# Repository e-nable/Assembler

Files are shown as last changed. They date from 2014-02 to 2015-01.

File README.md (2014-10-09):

e-NABLE Assembler (AKA Hand-o-Matic)
=======

repository for OpenSCAD scripts (and referenced STL files) for e-NABLE Assembler project

Overall control flow is:



This repository contains the Assembly.scad and it's dependencies, such as the STL files for all of the e-NABLE designs. These include:

- Assembly assembles parts from individual designs (below)
- Cyborg_Beast
- Parametric_Gauntlet
- Parametric Tensioner
- Parametric Knuckle Block
- David Finger
- Talon (placeholder)

Parameters
========
part
- 0 Assembled Model
- 1 Gauntlet
- 2 Palm
- 3 Finger Proximal (Near knuckle)
- 4 Finger Distal (Fingertip)
- 5 Thumb Proximal (Near knuckle)
- 6 Thumb Distal (Thumbtip)

Finger Style
- 1 Cyborg Beast
- 2 David
- 3 Creo Cyborg Beast

Palm Style
- 1 Cyborg Beast
- 2 Cyborg Beast Parametric
- 3 Creo Cyborg Beast

Example
======
openscad -o preview.png -D Left1=66.47 -D Left2=64.04 -D  Left3=46.95 -D  Left4=35.14 -D  Left5=35.97 -D  Left6=27.27 -D  Left7=31.80 -D  Left8=40.97 -D  Left9=31.06 -D  Left10=147.5 -D Right1=62.67 -D Right2=65.62 -D  Right3=59.14 -D  Right4=48.78 -D  Right5=51.85 -D  Right6=16.4 -D  Right7=0 -D  Right8=72.52 -D  Right9=72.23 -D  Right10=230.6  -D part=0 -D fingerSelect=1 -D palmSelect=2 -D WristBolt=5.5 -D KnuckleBolt=3.3 -D JointBolt=3.3 -D ThumbBolt=3.3   e-NABLE/Assembly/Assembly.scad

Prerequisites
=========
OpenScad as ran on command line. Download from openscad.org

On a 'headless' server, you may need to set up a virtual container for the program to render into. The code below is to be ran on the command line before you run the comand line openscad. It may not work on your server. A google search found this example, your system may need something else.

Xvfb :5 -screen 0 800x600x24 &
export DISPLAY=:5

See Also
=========
The e-NABLE Assembler is utilized by the e-NABLE Service Station (AKA Hand-o-Matic) at https://github.com/e-nable/Service-Station .

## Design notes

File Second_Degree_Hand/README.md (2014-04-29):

Second Degree Hand by David
===========================

http://www.thingiverse.com/thing:300499

This is a mechanical hand made for users with a functional thumb. It includes an opening that allows the user to utilize their thumb along with mechanical fingers.

This hand includes a couple of unusual features:

First, this hand allows for two degrees of freedom in the motion. Most similar hands only allow the user to raise or lower the fingers. This one also allows the user to move the fingers side-to-side. A demonstration of the two degrees of freedom can be seen at:

http://youtu.be/62XzqfjZZns

Second, this hand includes springs on the tuners. This resolves some issues so that the hand has dramatically improved grip. A demonstration of this feature can be seen at:

http://youtu.be/e6_-tVWOsLo

This design is also fully parametric OpenSCAD files. Although there are STL files attached, they are just for example purposes. The intention is that each individual will create their own unique STLs from the SCAD files.

There is currently no option for a mechanical thumb in this design. There are a couple of other hand designs that include a mechanical thumb. If someone really wants a thumb added to this design (maybe because of the two degrees of freedom) I can maybe add it.

I am not marking this one a work in progress. The one I was making for my sister is pretty much complete and working well. I am working on an updated version, but that will likely be a new version 3.

As always... This is provided in the hope that it will be beneficial. It is provided, however, without any warranty of any sort. Use at your own risk, and seek appropriate medical attention. If you do use it, and you experience any problems, immediately discontinue use.

For more information on where to connect with people who can help someone in need with sizing, printing and/or assembly of a mechanical hand please join the e-NABLE Google+ Community entitled, e-NABLE: 
https://plus.google.com/communities/102497715636887179986 
For more information and stories: 
http://enablingthefuture.org 
https://www.facebook.com/enableorganization

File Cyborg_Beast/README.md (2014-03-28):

e-nable : Cyborg Beast
======================

Repository for Cyborg Beast files.

- Blender Files are the source files
- STL files are rendered for printing
- OpenSCAD files assemble the STL files for parametric rendering

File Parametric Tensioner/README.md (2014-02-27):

Parametric Cable Tensioner
==========================

See http://www.thingiverse.com/thing:238852 for originals.

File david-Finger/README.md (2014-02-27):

Parametric Finger
=================

See http://www.thingiverse.com/thing:257544 for originals.

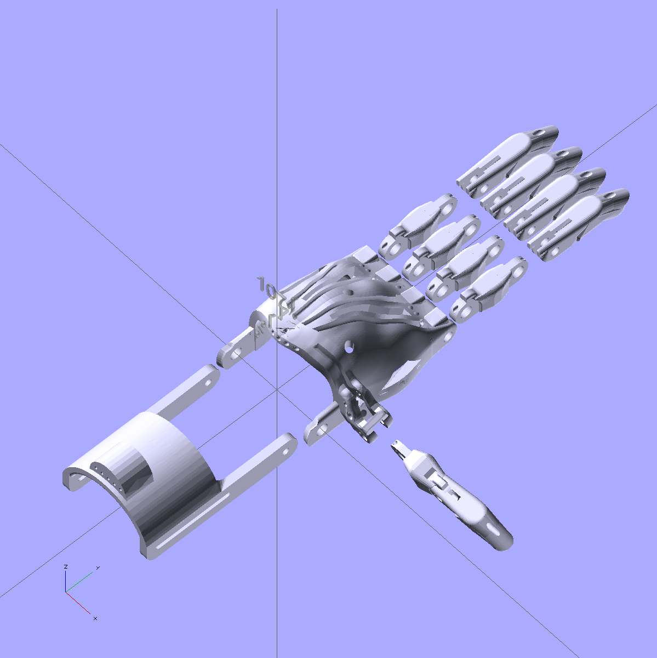
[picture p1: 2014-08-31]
explode2.png

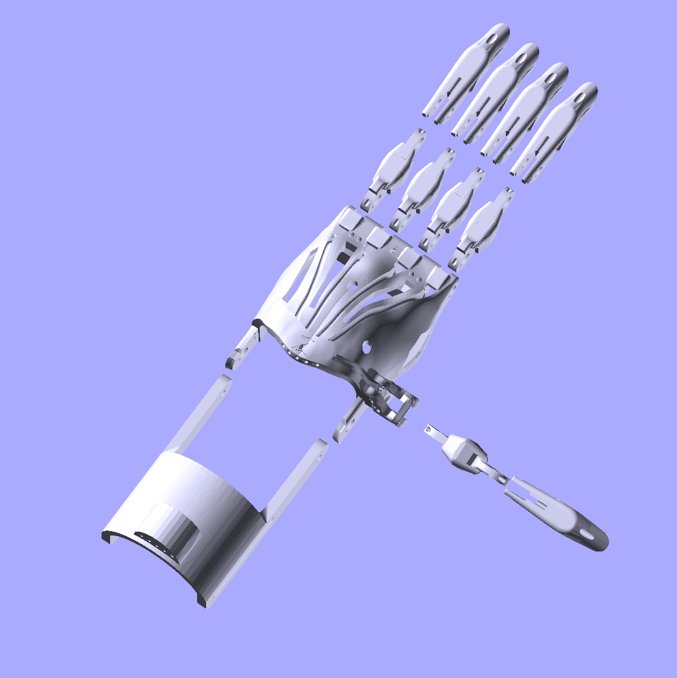
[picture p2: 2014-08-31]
exploded-image.png

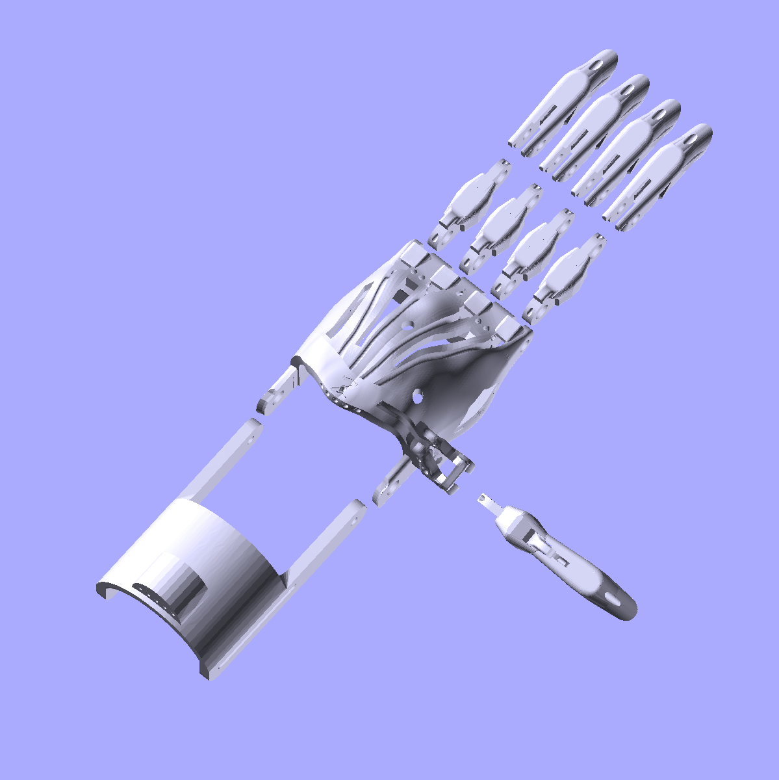
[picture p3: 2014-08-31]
explode3.png

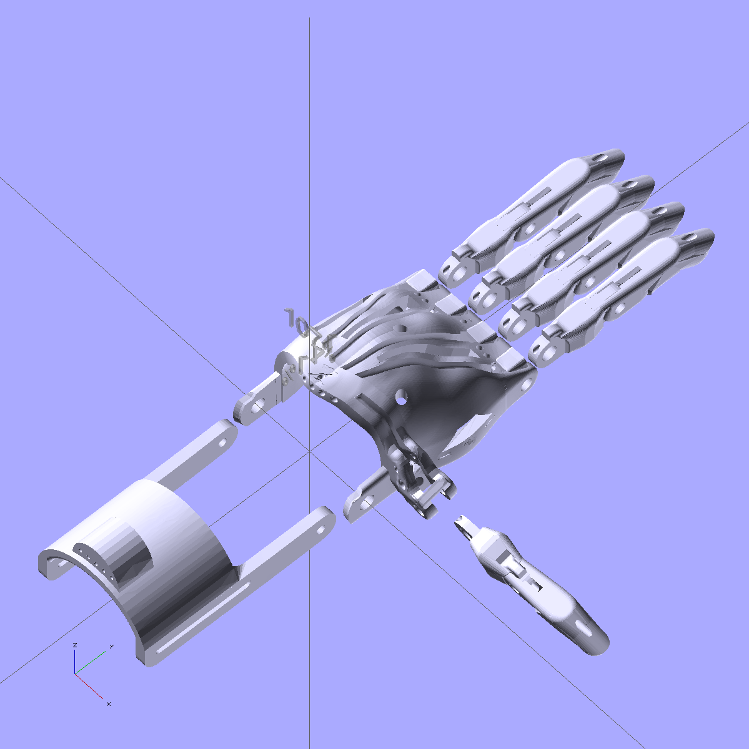
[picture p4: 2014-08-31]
exploded.png

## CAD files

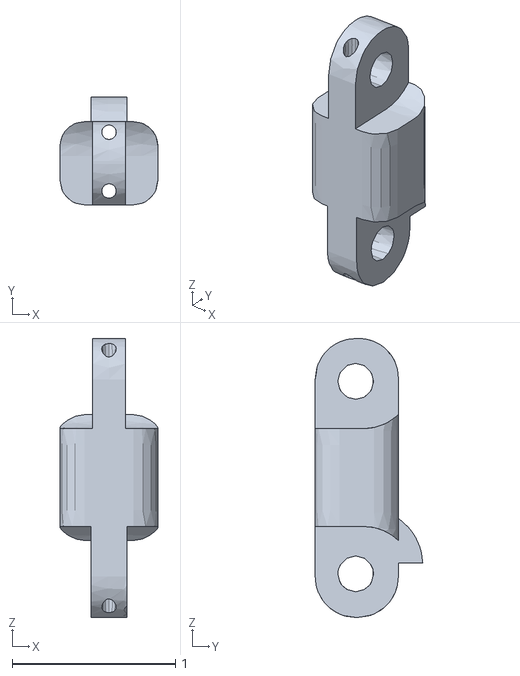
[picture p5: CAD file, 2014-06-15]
Cyborg_Beast/Creo_Cyborg_Beast/finger_mid_joint.stl
0.6 x 0.66 x 1.71

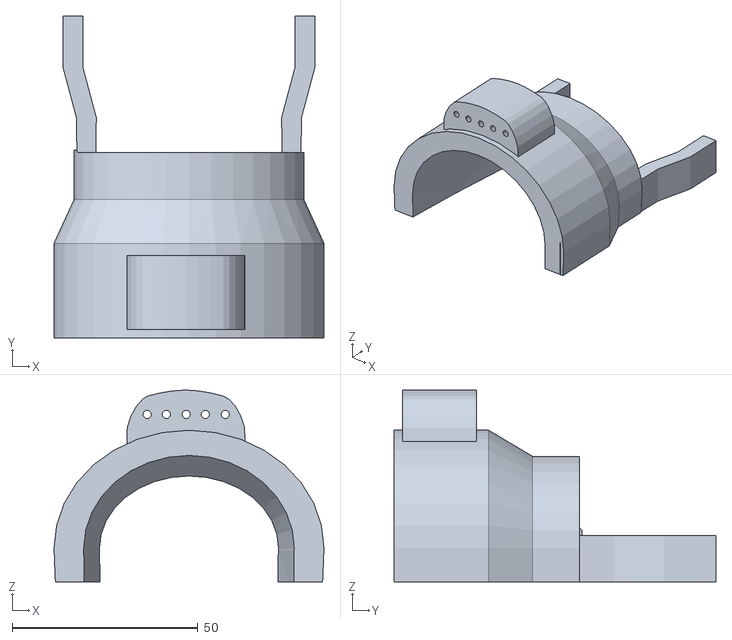
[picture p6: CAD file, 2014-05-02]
Cyborg_Beast/STL Files/Cyborg Hand 1.2/Cyborg gauntlet 1.2 (Ivan).stl
72.7 x 86.6 x 51.7

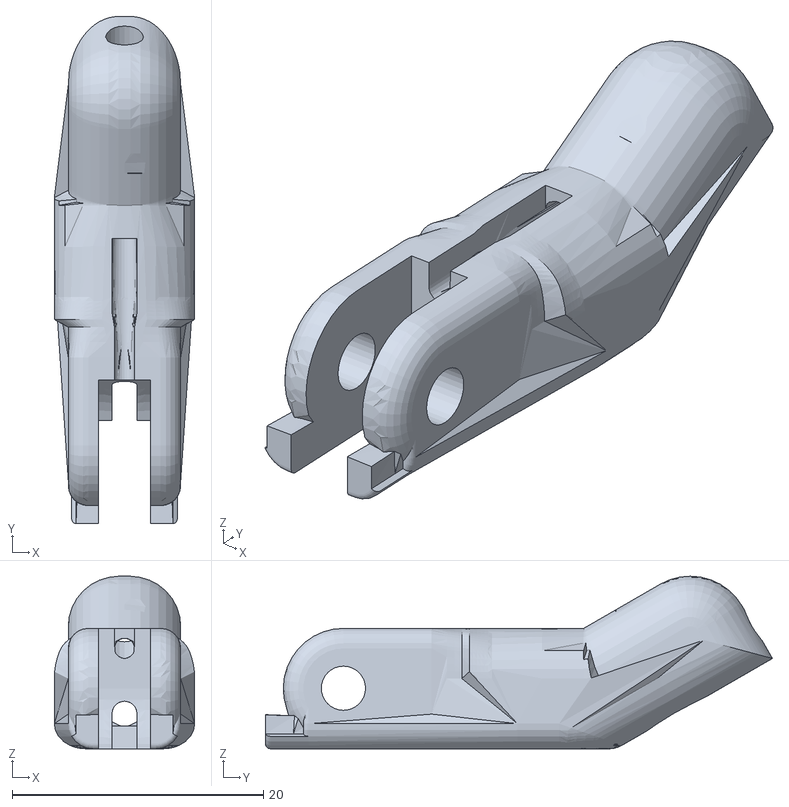
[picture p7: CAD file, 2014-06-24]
Cyborg_Beast/STL Files/Cyborg Hand 1.4/CB Finger 1.41 (no bumps).stl
11.2 x 40.3 x 13.7

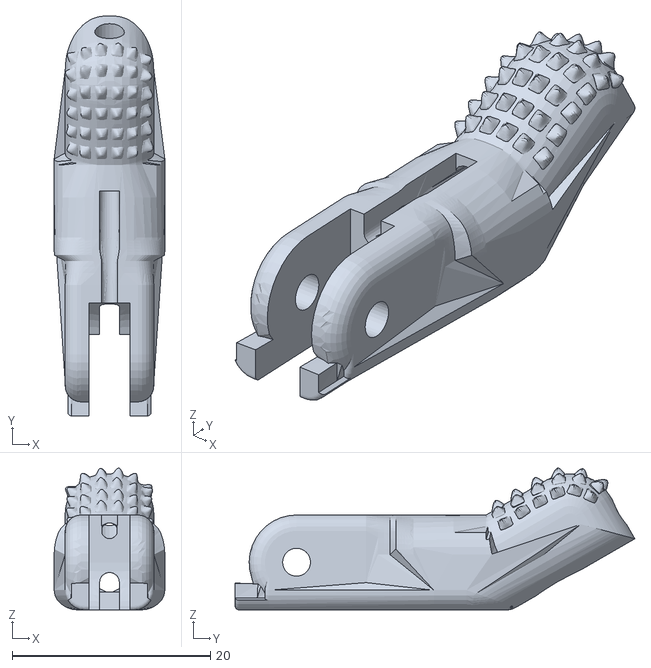
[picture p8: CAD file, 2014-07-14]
Cyborg_Beast/STL Files/Cyborg Hand 1.45 No Thumb/CB_Finger (bumps) Non-Manifold 1.45.stl
11.2 x 40.3 x 14.3

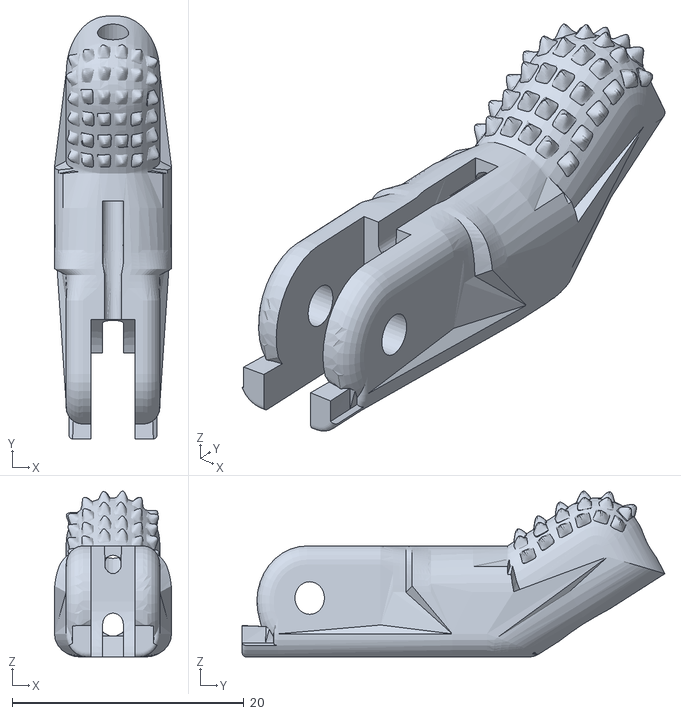
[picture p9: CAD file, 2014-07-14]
Cyborg_Beast/STL Files/Cyborg Hand 1.45/CB_Thumb_Finger (bumps) Non-Manifold 1.45.stl
10.1 x 36.5 x 14.3

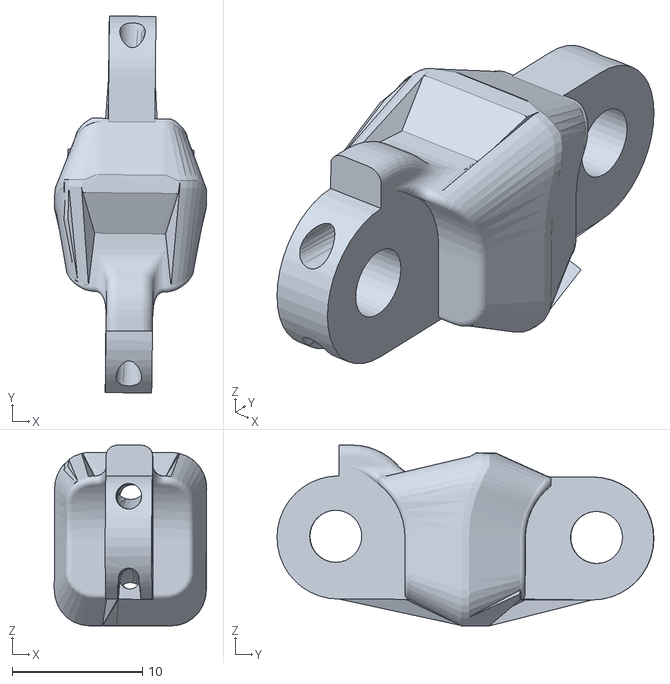
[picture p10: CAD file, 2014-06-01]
Cyborg_Beast/STL Files/Cyborg_Beast_Peter_Binkleys_Fix/ProxThumb.stl
11.7 x 28.9 x 13.9

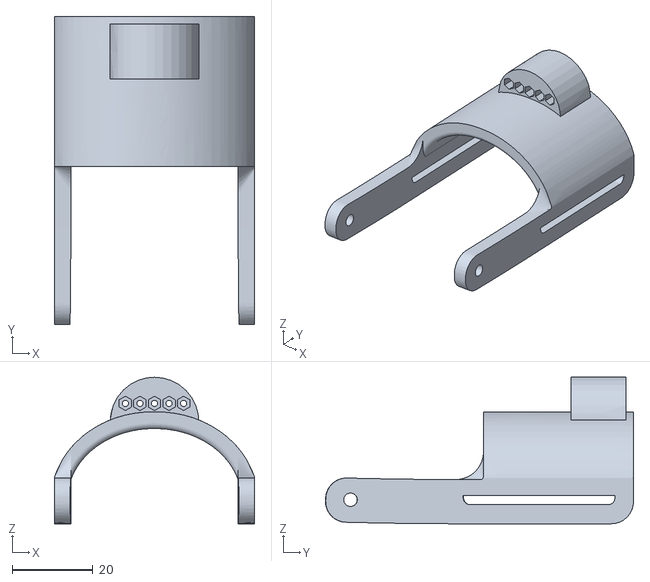
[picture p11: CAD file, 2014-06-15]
Cyborg_Beast/STL Files/Karunas_Short_Gauntlet.stl
49.6 x 76.3 x 36.3

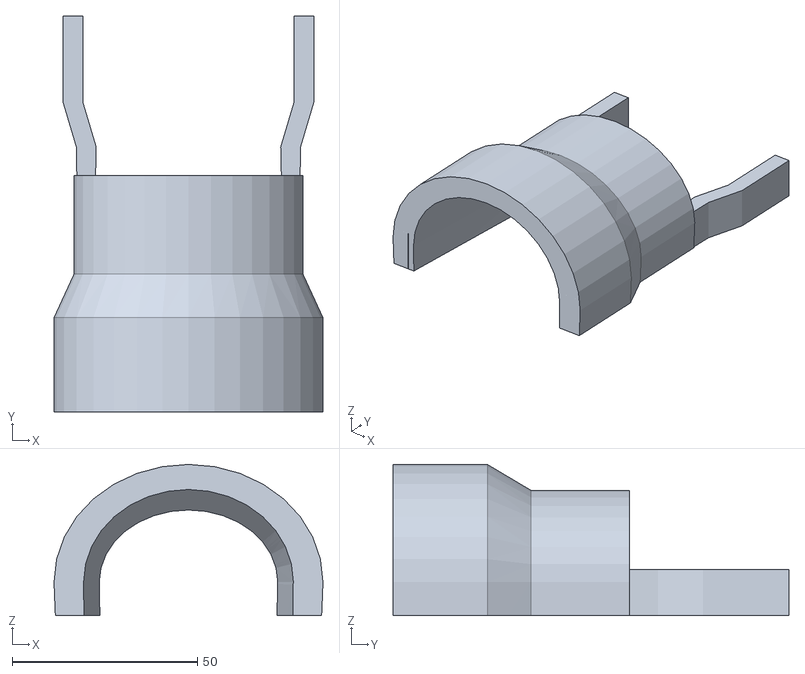
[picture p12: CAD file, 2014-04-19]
Cyborg_Beast/STL Files/STL Files_ Marc Petrykowski_4-16-2014/Cyborg Gauntlet 1.1.stl
72.7 x 106.9 x 40.8

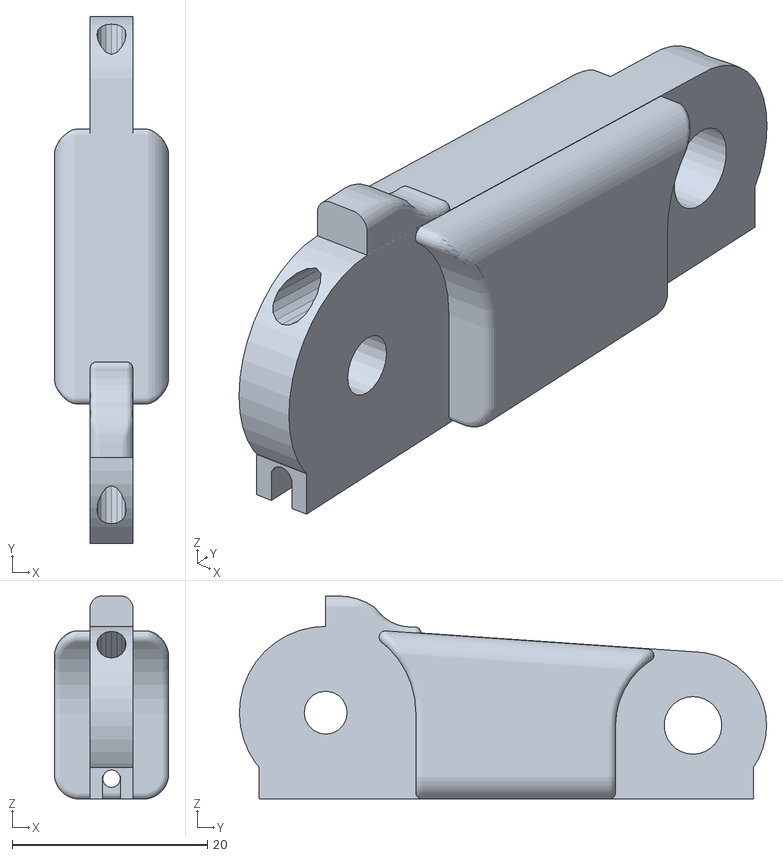
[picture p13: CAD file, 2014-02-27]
david-Finger/David-FingerProximal-Index.stl
11.7 x 54.0 x 20.8

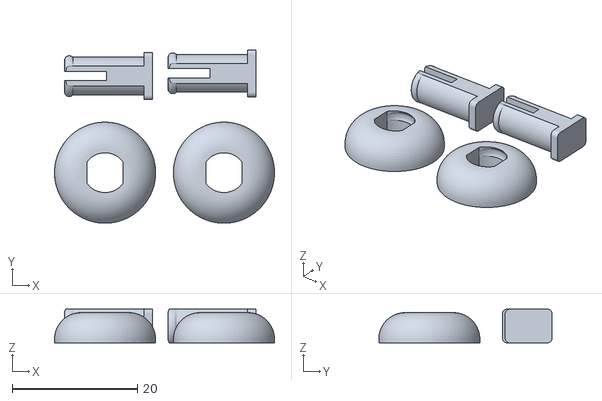
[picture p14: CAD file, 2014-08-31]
EH2.0/non-aligned/EH2.0_Gauntlet_Ware_2.5 (2 of 3).stl
35.2 x 27.7 x 5.40

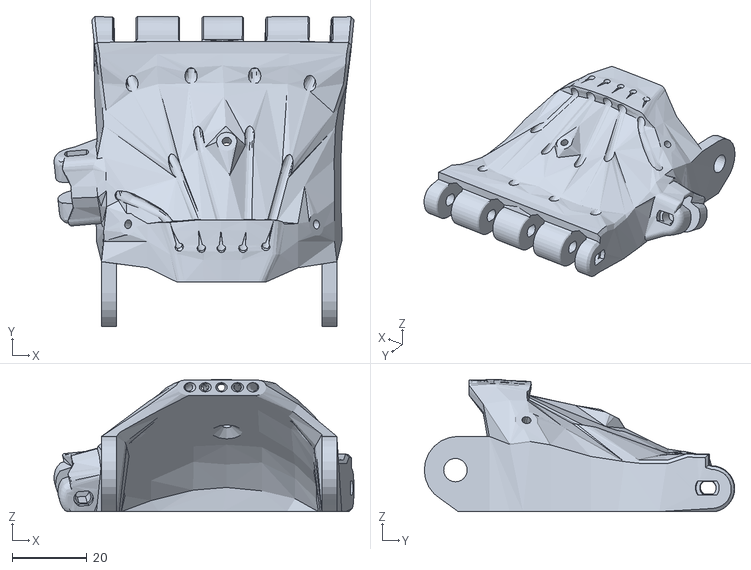
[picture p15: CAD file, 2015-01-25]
EH2.0/RaptorPalmRightNoSup_2.22.stl
80.3 x 83.1 x 35.4

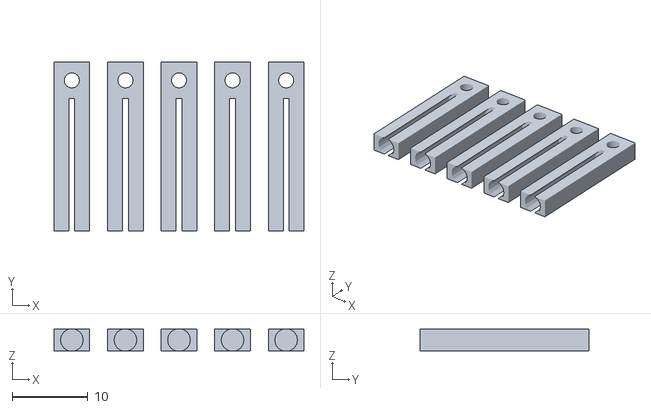
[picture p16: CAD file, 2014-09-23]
EH2.0/TensionerPins/TensionerPins-3mm.stl
32.9 x 22.2 x 2.85

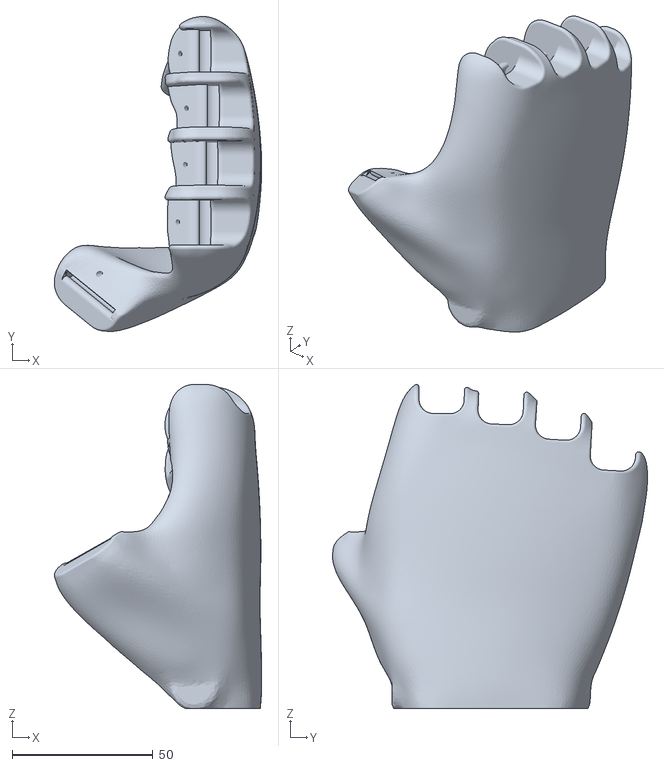
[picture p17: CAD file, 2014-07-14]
Flexy-Hand_2-2/Hand_Body_-_RH.stl
73.6 x 111.7 x 114.9

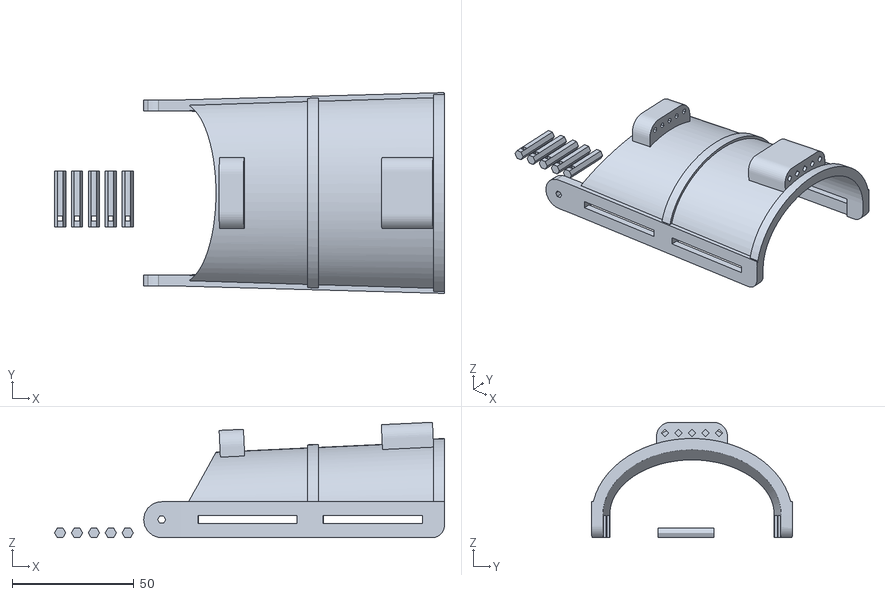
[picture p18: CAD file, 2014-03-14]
Parametric_Gauntlet/David-Gauntlet-5M2.stl
160.0 x 82.4 x 47.4

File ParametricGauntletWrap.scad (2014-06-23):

/* [Measurements] */
// See Measurement Guide at:
// https://docs.google.com/a/popk.in/document/d/1LX3tBpio-6IsMMo3aaUdR-mLwWdv1jS4ooeEHb79JYo for details.
// The default values are the ones from the photo in that document.

// e-NABLE measurement 5, Wrist Joint distance from lateral to medial side
wrist = 35.97;
// Length of gauntlet, e.g. half distance from elbow to wrist.
len = 100;
// Distance between lateral and medial side of the middle forearm (end of gauntlet closest to elbow)
width = 46.35;
// height of side rail
rail = 10; 
// thickness of side rails
thick=5; 
// thickness of rest of gauntlet
thin=2; 
// thickness of padding
padding = 5;
// spacing of bars
spacing = 10;
// thickness of bars
bar=5;
// diameter of bolt for wrist pivot
bolt = 5;
// Length of slots
slotLen = 25;
// Height of slots
slotH = 2;

/* [hidden] */

pi=3.1415926;

wristX = (wrist+2*padding)*pi/2-rail/2;
wideX = (width+2*padding)*pi/2-rail/2;

diff = wideX-wristX;
angle = atan(diff/len);
echo(diff,angle);

echo(len, wristX, wideX);

difference() {
union() {
difference() {
	union() {
		hull() {
			translate([wristX,0]) cylinder(d=rail, h=thick);
			translate([wideX,-len]) cylinder(d=rail, h=thick);
			}
		hull() {
			translate([-wristX,0]) cylinder(d=rail, h=thick);
			translate([-wideX,-len]) cylinder(d=rail, h=thick);
			}
		scale([3,1,1])hull() {
			translate([0,-(wristX)]) cylinder(d=rail, h=thin);
			translate([0,-len]) cylinder(d=rail, h=thin);
			}
		difference() {
			hull() {
				translate([wristX,-bar]) cylinder(d=rail, h=thin);
				translate([wideX,-len]) cylinder(d=rail, h=thin);
				translate([-wristX,-bar]) cylinder(d=rail, h=thin);
				translate([-wideX,-len]) cylinder(d=rail, h=thin);
				}
			translate([0,0,-1]) cylinder(r=wristX-rail/2, h=thick+2);
			translate([0,0,-.5]) for (r=[wristX-rail/2+bar:spacing:len+3*spacing]) {
				core(r,bar,thin+1);
				}
			}
		}
	}

hull() {
	translate([-wideX,-len]) cylinder(d=rail, h=thin);
	translate([wideX,-len]) cylinder(d=rail, h=thin);
	}
}
	translate([wristX,0,-2]) cylinder(d=bolt, h=thick+4);
	translate([-wristX,0,-2]) cylinder(d=bolt, h=thick+4);
	translate([wideX,-len,-1]) rotate([0,0,angle]) cube([2,25,thick+2]);
	translate([-wideX-slotH,-len,-1]) rotate([0,0,-angle]) cube([2,25,thick+2]);
	translate([wideX-diff/3,-len*.67,-1]) rotate([0,0,angle]) cube([slotH,25,thick+2]);
	translate([-wideX+diff/3-slotH,-len*.67,-1]) rotate([0,0,-angle]) cube([slotH,25,thick+2]);
	translate([wideX-diff*.67,-len/3,-1]) rotate([0,0,angle]) cube([slotH,25,thick+2]);
	translate([-wideX+diff*.67-slotH,-len/3,-1]) rotate([0,0,-angle]) cube([slotH,25,thick+2]);

}


module core(r,t,h) {
	difference() {
		cylinder(r=r+t, h=h);
		translate([0,0,-1]) cylinder(r=r, h=h+1);
		}
	}

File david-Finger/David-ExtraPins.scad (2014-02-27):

/*

Extra Pins for Parametric Fingers
By David Orgeman

licensed under the Creative Commons - Attribution - Share Alike license

This program is distributed in the hope that it will be useful,
but WITHOUT ANY WARRANTY; without even the implied warranty of
MERCHANTABILITY or FITNESS FOR A PARTICULAR PURPOSE.

*/



//PARAMETERS

//Pin_Head_Height is the size of the thickness of the head on the pin.
Pin_Head_Height=1.4;

//Knuckle_Hole_Size is the hole for the link between distal and proximal phalanges.  Set this
//to the diameter or the pin.  Pins with larger diameter work better.
Knuckle_Hole_Size=5.0;

//Set Scale_Factor to match the scaling of the other prosthetic parts.
Scale_Factor=1.3;


//RENDER

translate([20, -10, 0])
	custom_pin();
translate([0, -10, 0])
	custom_pin();
translate([-20, -10, 0])
	custom_pin();
translate([10, 10, 0])
	custom_pin();
translate([-10, 10, 0])
	custom_pin();


module custom_pin()
	{
	pin_horizontal(h=9*Scale_Factor, lh=1.7, lt=1.0, r=Knuckle_Hole_Size/2, tight=false);
	translate([0, 9*Scale_Factor/2, (Knuckle_Hole_Size-0.5)/2])
		rotate(a=[90, 0, 0])
			difference()
				{
				cylinder(h=Pin_Head_Height, r=1.5*Knuckle_Hole_Size/2, $fn=16);
				translate([-5, -10-Knuckle_Hole_Size/2+0.375, -5])
					cube([10, 10, 10]);
				translate([-5, Knuckle_Hole_Size/2-0.375, -5])
					cube([10, 10, 10]);
				}
	}

	
	
module fillet(r, h) 
	{
	translate([r/2, r/2, 0])
		difference() 
			{
			cube([r, r, h], center=true);
			translate([r/2, r/2, 0])
				cylinder(h=h+1, r=r, center=true, $fn=40);
			}
	}



module fillet_bez(r, h, a=90) 
	{
	p0=[r, 0];
	p1=[0, 0];
	p2=[r*cos(a), r*sin(a)];
	translate([0, 0, -h/2])
		linear_extrude(height=h) BezConic(p0, p1, p2, 32);
	}



//Polyhole module by nophead
//licensed under the Creative Commons - Attribution license
//provided here, as-is, without any warranty of any sort
//original work available at http://www.thingiverse.com/thing:6118
//and also at http://hydraraptor.blogspot.com/2011/02/polyholes.html

module polyhole(d, h) 
	{
	n=max(round(2*d), 3);
	rotate(v=[0, 0, 180])
		cylinder(h=h, r=(d/2)/cos(180/n), center=true, $fn=n);
	}



//OpenSCAD Conic Bezier Curve by donb
//licensed under the Creative Commons - Public Domain license - no rights reserved
//provided here, as-is, without any warranty of any sort
//original work available at http://www.thingiverse.com/thing:8931

/* 
Conic Bezier Curve
also known as Quadratic Bezier Curve
also known as Bezier Curve with 3 control points 

Please see 
http://www.thingiverse.com/thing:8443 by William A Adams
http://en.wikipedia.org/wiki/File:Bezier_2_big.gif by Phil Tregoning
http://en.wikipedia.org/wiki/B%C3%A9zier_curve by Wikipedia editors

By Don B, 2011, released into the Public Domain
*/

module BezConic(p0, p1, p2, steps=5) {

	stepsize1 = (p1-p0)/steps;
	stepsize2 = (p2-p1)/steps;

	for (i=[0 : steps-1]) {
		assign(point1 = p0+stepsize1*i) 
		assign(point2 = p1+stepsize2*i) 
		assign(point3 = p0+stepsize1*(i+1))
		assign(point4 = p1+stepsize2*(i+1))  {
			assign( bpoint1 = point1+(point2-point1)*(i/steps) )
			assign( bpoint2 = point3+(point4-point3)*((i+1)/steps) ) {
				polygon(points=[bpoint1, bpoint2, p1]);
			}
		}
	}
}



//"PLA Pin Connectors v2" by whpthomas
//licensed under the Creative Commons - Attribution - Share Alike license
//modified so the module creates a rounder pin at small sizes
//modified to make some primitives overlap so that the stl has fewer errors
//provided as-is, without any warranty of any sort
//original work available at http://www.thingiverse.com/thing:130879

// PLA Pin Connectors
// WHPThomas <me@henri.net>
// Derived to provide a drop in replacement for Tony Buser's pin connectors <tbuser@gmail.com>

//pinhole(h=12, tight=false);
//test();
//pintack(h=20);
//pinpeg(h=24);

module test() {
  tolerance = 0.2;
  radius=7/2;
  
  translate([-12, 16, 0]) pinpeg(h=21, r=radius);
  translate([12, 12, 0]) pintack(h=12, r=radius);
  
  difference() {
    union() {
      translate([0, -12, 2.5]) cube(size = [60, 20, 5], center = true);
      translate([24, -12, 7.5]) cube(size = [12, 20, 15], center = true);
    }
    translate([-24, -12, 0]) pinhole(h=5, r=radius, t=tolerance);
    translate([-12, -12, 0]) pinhole(h=5, r=radius, t=tolerance, tight=false);
    translate([0, -12, 0]) pinhole(h=16, r=radius, t=tolerance);
    translate([12, -12, 0]) pinhole(h=16, r=radius, t=tolerance, tight=false);
    translate([24, -12, 15]) rotate([0, 180, 0]) pinhole(h=12, r=radius, t=tolerance);
  }
}

module pinhole(h=16, r=4, lh=3, lt=1, t=0.3, tight=true) {
  // h = shaft height
  // r = shaft radius
  // lh = lip height
  // lt = lip thickness
  // t = tolerance
  // tight = set to false if you want a joint that spins easily
  union() {
    pin_solid(h, r+(t/2), lh, lt);
    if (tight) {
      // make the cylinder slightly longer
      cylinder(h=h+t, r=r, $fn=30);
    }
    else {
      // make the cylinder slightly longer and wider
      cylinder(h=h+t, r=r+(t/2)+t, $fn=30);
    }
    // camfer the entrance hole to make insertion easier
    translate([0, 0, -0.1]) cylinder(h=lh/3, r2=r, r1=r+(t/2)+(lt/2), $fn=30);
  }
}

module pin(h=16, r=4, lh=3, lt=1, side=false) {
  // h = shaft height
  // r = shaft radius
  // lh = lip height
  // lt = lip thickness
  // side = set to true if you want it printed horizontally
  hh = h < 2.5*r ? 2.5*r : h;
  if(h < 2.5*r) echo("****** WARNING: pin caped at minimum length ", h, "set to", hh);

  if (side) {
    pin_horizontal(hh, r, lh, lt);
  } else {
    pin_vertical(hh, r, lh, lt);
  }
}

module pintack(h=16, r=4, lh=3, lt=1, bh=3, br=8.75) {
  // bh = base_height
  // br = base_radius
  
  union() {
    cylinder(h=bh, r=br);
    translate([0, 0, bh]) pin(h, r, lh, lt);
  }
}

module pinpeg(h=32, r=4, lh=3, lt=1, t=0.1, tabs=false) {
  // h = shaft height
  // r = shaft radius
  // lh = lip height
  // lt = lip thickness
  // t = tolerance
  hh = h < 6*r ? 6*r : h;
  if(h < 6*r) echo("****** WARNING: pinpeg caped at minimum length ", h, "set to", hh);
  union() {
    translate([0, -hh/4+t/2, 0]) pin_horizontal(hh/2+t, r, lh, lt);
    translate([0, hh/4-t/2, 0]) rotate([0, 0, 180]) pin_horizontal(hh/2+t, r, lh, lt);
	if(tabs) {
		translate([0, hh*3/8, 0]) cylinder(h=0.15, r=2*r);
		translate([0, -hh*3/8, 0]) cylinder(h=0.15, r=2*r);
	}
  }
}

// just call pin instead, I made this module because it was easier to do the rotation option this way
// since openscad complains of recursion if I did it all in one module
module pin_vertical(h=16, r=4, lh=3, lt=1) {
  // h = shaft height
  // r = shaft radius
  // lh = lip height
  // lt = lip thickness
  cl=r*2.1;
  cz=h-(r*2);
  difference() {
    pin_solid(h, r, lh, lt, false);
    
    // center cut
    translate([-r*0.5/2, -(r*2+lt*2)/2, cz]) cube([r*0.5, r*2+lt*2, cl]);
    translate([0, 0, cz]) 
    scale(v=[1,r/(r+lt)*1.05,1]){
       sphere(r=r*1/2, $fn=20);
       cylinder(h=cl, r1=r*1/2, r2=r*4/5, $fn=20);
    }
    // center curve
    translate([0, 0, cz]) rotate([90, 0, 0]) cylinder(h=cl, r=r/4, center=true, $fn=20);
  
    // side cuts
//    translate([-r*2, -lt-r*1.125, -1]) cube([r*4, lt*2, h+2]);
//    translate([-r*2, -lt+r*1.125, -1]) cube([r*4, lt*2, h+2]);
    translate([-r*2, -lt-r*1.25, -1]) cube([r*4, lt*2, h+2]);
    translate([-r*2, -lt+r*1.25, -1]) cube([r*4, lt*2, h+2]);
  }
}

// call pin with side=true instead of this
module pin_horizontal(h=16, r=4, lh=3, lt=1) {
  // h = shaft height
  // r = shaft radius
  // lh = lip height
  // lt = lip thickness
//  translate([0, h/2, r*1.125-lt]) rotate([90, 0, 0]) pin_vertical(h, r, lh, lt);
  translate([0, h/2, r*1.3-lt]) rotate([90, 0, 0]) pin_vertical(h, r, lh, lt);
}

// this is mainly to make the pinhole module easier
module pin_solid(h=16, r=4, lh=3, lt=1, hole=true) {
  union() {
    // shaft
    cylinder(h=h-(lh/2), r=r, $fn=30);
    // lip
    if(hole) {
      translate([0, 0, h-lh]) cylinder(h=lh*0.25, r1=r, r2=r+lt, $fn=30);
//      translate([0, 0, h-lh]) cylinder(h=lh*0.25, r=r+lt, $fn=30);
      translate([0, 0, h-lh+lh*0.25-0.01]) cylinder(h=lh*0.25+0.02, r=r+lt, $fn=30);    
      translate([0, 0, h-lh+lh*0.5]) cylinder(h=lh*0.5, r1=r+lt, r2=r, $fn=30);
    }
    else {
      scale(v=[1,r/(r+lt)*1.05,1]) {
        translate([0, 0, h-lh]) cylinder(h=lh*0.25, r1=r, r2=r+(lt*2/3), $fn=30);
//        translate([0, 0, h-lh+lh*0.25]) cylinder(h=lh*0.25, r=r+(lt*2/3), $fn=30);    
        translate([0, 0, h-lh+lh*0.25-0.01]) cylinder(h=lh*0.25+0.02, r=r+(lt*2/3), $fn=30); 
        translate([0, 0, h-lh+lh*0.50]) cylinder(h=lh*0.50, r1=r+(lt*2/3), r2=r-(lt/2), $fn=30);
      }
    }
  }
}

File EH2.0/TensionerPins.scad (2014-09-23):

// Generate tensioner blocks. for e-NABLE Hand 2.0.

// reference a few related objects from the EH2.0 to check fit:

//import("/Users/laird/src/e-NABLE-Assembler/EH2.0/EH2.0_Tensioner [x1].stl");

//%difference() {
//	import("/Users/laird/src/e-NABLE-Assembler/EH2.0/Hexpins_2.6.stl");
//	}

x=4.7;
y=22.2;
z=2.85;
d=2;
o=2.4;
screwD = 2.4;
	
tensioners(2.25);

module tensioners(screwD=2.4) {
	assign(spacing=1.5*x) {
	echo(screwD, spacing);
	for (x2 = [-2*spacing:spacing:2*spacing]) translate([x2,0,0]) tensionerPin(screwD);
	}
}

module tensionerPin(screwD=2.4) {
	difference() {
		translate([0,0,z/2]) cube([x,y,z], center=true);
		translate([0,y/2-o,-1]) cylinder(d=d,h=20, $fn=16);
		translate([0,y/2-2*o,z/2]) rotate([90,0,0]) cylinder(d=screwD,h=20, $fn=16);
	}
	}

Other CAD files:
Assembly/write/orbitron.dxf
Cyborg_Beast/STL Files/Cyborg Hand 1.3/Cyborg gauntlet 1.3 (Ivan).stl
Cyborg_Beast/STL Files/STL Files (Marc Petrykowsk)/Cyborg Thumb Phalange 1.0.stl
RaptorReloaded/raptor_reloaded_knuckle_pin.stl
Parametric_Gauntlet/Include-HandParameters.scad
Assembly/Assembly.scad
Assembly/Creo Cyborg Finger.scad
Assembly/Creo Cyborg Proximal Phalange.scad
Assembly/CreoCyborgLeftPalm.scad
Assembly/CreoCyborgThumbFinger.scad
Assembly/CreoCyborgThumbPhalange.scad
Assembly/Cyborg Finger.scad
Assembly/Cyborg Gauntlet.scad
Assembly/Cyborg Proximal Phalange.scad
Assembly/CyborgLeftPalm.scad
Assembly/CyborgNTLeftPalm.scad
Assembly/CyborgThumbFinger.scad
Assembly/CyborgThumbPhalange.scad
Assembly/EH2Fingertip.scad
Assembly/EH2Gauntlet.scad
Assembly/EH2LeftPalm.scad
Assembly/EH2Parts.scad
Assembly/EH2ProximalPhalange.scad
Assembly/KarunaGauntlet.scad
Assembly/ModelArm.scad
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

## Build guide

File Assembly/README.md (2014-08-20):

e-NABLE : Assembly
==================

Command line tool that assembles parts from individual designs.

For STL files, it loads a component wrapper (in this directory) that loads the STL and performs required scaling,
translation, etc., to fit the component into the assembly. See CyborgLeftPalm.scad for an example.

For parametric designs, it loads the design as an <import> followed by calling the module that renders the part. See ../Cyborg_Beast/OpenSCAD Files/cyborgbeast07e.scad as an example.

Currently integrated designs are:

- Assembler source is https://github.com/e-nable/e-NABLE-Assembler
- Cyborg Beast http://www.thingiverse.com/thing:261462 by JorgeZuniga, verson 1.4 by Marc Petrykowski 
- Creo version of Cyborg Beast http://www.thingiverse.com/thing:340750 by Ryan Dailey
- Parametric Gauntlet from http://www.thingiverse.com/thing:270259 by David Orgeman
- Cyborg Beast Short Gauntlet (Karuna's Gauntlet) http://www.thingiverse.com/thing:270322 by Frankie Flood 
- Parametric Finger v2  http://www.thingiverse.com/thing:257544 by David Orgeman

This program assembles the components from various e-NABLE designs, and scales and arranges them based on measurements.

License
=======

    Copyright (C) 2014, Laird Popkin

    This program is free software: you can redistribute it and/or modify
    it under the terms of the GNU Affero General Public License as
    published by the Free Software Foundation, either version 3 of the
    License, or (at your option) any later version.

    This program is distributed in the hope that it will be useful,
    but WITHOUT ANY WARRANTY; without even the implied warranty of
    MERCHANTABILITY or FITNESS FOR A PARTICULAR PURPOSE.  See the
    GNU Affero General Public License for more details.

    You should have received a copy of the GNU Affero General Public License
    along with this program.  If not, see <http://www.gnu.org/licenses/>.

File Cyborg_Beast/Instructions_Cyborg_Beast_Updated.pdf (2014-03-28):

E-NABLE 1

MANUAL

*If you need assistance, please contact the E-NABLE GROUP. https://www.facebook.com/#!/enableorganization

http://enablingthefuture.org/our-tree/

https://plus.google.com/u/0/communities/102497715636887179986

Description

The Cyborg Beast is a remix of the snap together Robohand and the original Robohand . Most voluntary closing devices including this design need sufficient wrist movement and strength for proper function. This design doesn’t require Orthoplastic. The fingers are designed for better griping and to avoid over extension of the proximal phalange and distal finger segment. It fits a 1 to 2 mm cabling and elastic bands. This design is compatible with any version of the MakerBot MakerWare software and any of the MakerBot Replicator printers. This design was developed using Blender 2.69.

Printing Instructions

Best quality is obtained using ABS plastic with rafts and supports. The proximal phalanges and finger STL files contain one element. Please add or duplicate as needed on the building platform. The thumb phalange and distal finger segment are slightly different that the rest of the fingers. You can replace the thumb parts with the regular finger parts if you need to increase the length of the thumb.

Sizing (adapted from the Snap Together Robohand Instruction Manual http://www.thingiverse.com/thing:92937)

Overview: to get a perfect fit, you will be scaling all the parts of the hand by a percentage, based upon the size of the user’s hand.

- Measure the knuckle area of the non-affected hand in centimeters or inches. If you measured inches, multiply your number by 2.54 to obtained centimeters.
- Convert centimeters to millimeters by multiplying your number times 10.

Acknowledgements:

Thank you to all members of the E-NABLE group, The Creighton University Group, The University of Wisconsin–Milwaukee Group, and Robohand. This updated version includes modifications from Ivan Owen, Peter Binkley, and Jorge Zuniga. Special thanks you to our beta testers and makers Gregg Dennison, Frankie Flood, and Paul & Leon McCarthy.

- Add 5mm to your measurement to account for the thickness of the Velcro based gauntlet.
- (Example: if the individual’s hand measures 3 inches, then you will take 3 x 2.54 = 7.62 cm, then multiply this number times 10, so you will get 76.2 mm, add 5mm for the Velcro based gauntlet and you will get a total length of 81.2 mm).
- The knuckle with in the files you downloaded is 55 mm. Divide your result by
- 55. (Example: 81.2/55 = 1.48 rounded)
- Multiply the answer times 100 to get a percentage.
- (Example: 1.48 x100 = 148%)
- Scale all the parts of the Cyborg Beast by this percentage before printing. This can be done using the ‘Scale’ tool in Makerware.
- Print all the components at the same scale.
*We found that for sizes less than 130% of the original the holes size may compromise the structure of the Cyborg Beast. We are in the process of developing plastic pins to replace the Chicago Screws in the finger joints.

Assembly Materials

For assembly you will need:

- Chicago screws (www.chicagoscrews.com).
- Aluminum Chicago Screws – 3’’ to 3 1/4"(or larger) for the knuckle. Size will depend on the width of the hand. You need 1 per hand.
- Stainless Steel Chicago Screws - 3/16" Blind or 1/4" for Velcro based gauntlets (hand and forearm). The specific size would depend of thickness of the Velcro. You need 6 of these.
- Stainless Steel Chicago Screws 3/8" – for wrist hinge/joint and 1/2’’ for the fingers. You need two 3/8’’ for the wrist hinge/joint and five 1/2 ‘’ for the fingers. For the wrist Chicago screws, include a plastic washer (see STL files) on each 3/8’’ Chicago screw post. The stainless Steel Chicago screws for the finger can be replaced by Aluminum Chicago Screws.
- Genuine Velcro 30' Length x 2" Width. It is sold by the roll, but you need about 24’’ inches. (http://www.amazon.com/dp/B006AWFGJ2/ref=pe_385040_30332200_pe_309540_26725410_item) (http://www.amazon.com/dp/B006AWFGJ2/ref=pe_385040_30332200_pe_309540_26725410_item)
- Shade Cord (Or Lift Cord) 0.9 mm (http://www.amazon.com/Roll-Yards-Shade-Cord-Lift/dp/B006DDHVM8). (http://www.amazon.com/Roll-Yards-Shade-Cord-Lift/dp/B006DDHVM8) It is sold by a roll of 100 yards, but you need about 2 yards.
- 2mm Black Elastic Bead Cord (http://shop.hobbylobby.com/products/2mm-black-elastic-beadcord-183418/). (http://shop.hobbylobby.com/products/2mm-black-elastic-bead-cord-183418/) It is sold by a roll of 5 yards, but you need only 1 yard.
- Firm Foam Padding. Sold by a roll of 25’ feet, but you only need 1 foot. (http://www.pattersonmedical.com/app.aspx?cmd=getProductDetail&key=070_921018416)
- Sleeve arm protector (http://www.expressmedicalsupplies.com/derma-sciences-glensleevearm-protectors-p-10193.html) (http://www.expressmedicalsupplies.com/derma-sciences-glensleeve-arm-protectors-p-10193.html)

Assembly instructions

Note: You may need to drill the holes a little bit to increase their size so the Chicago screw fit properly. Due to scaling the size of the holes get distorted.

1. Place -1/2" Chicago screws in finger (Figure 1) and 3’’ to 3 1/4"(or larger) Chicago screw in knuckle joints (Figure 2). It is recommended to place Teflon tape (http://www.amazon.com/Teflon-Tape-1-2-in/dp/B00004TZP8 ) on the treads to firm the screws so they don’t come loose. Ensure fingers move smoothly. If not, clean holes and remove plastic residues from the support plastic structure.

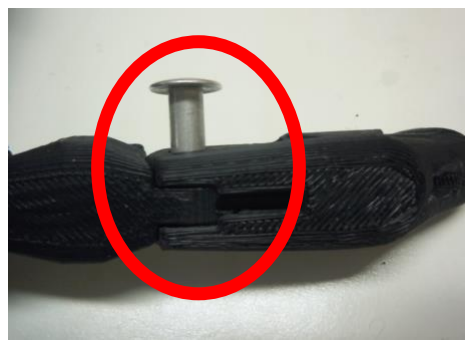
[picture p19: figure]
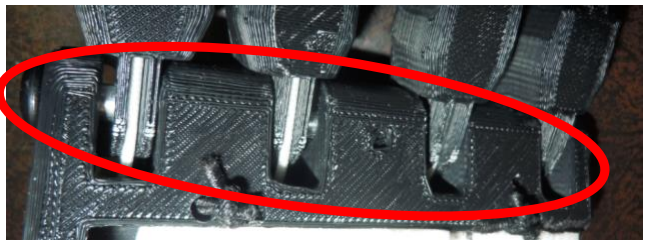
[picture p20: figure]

2. Cut and apply adhesive firm foam padding on the sides of the forearm gauntlet (Figure 3 and 4), back of the knuckle area (front part of the hand, see Figure 5), and any other are that may be in contact with the skin.
Figure 1. Finger Chicago Screw (1/2’’) | Figure 2. Knuckle Chicago Screw (3’’ to 3 1/4"or larger)

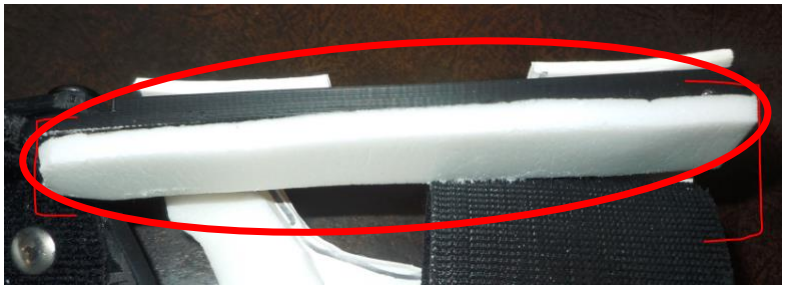
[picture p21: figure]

Figure 3. Gauntlet with firm foam padding (one side)

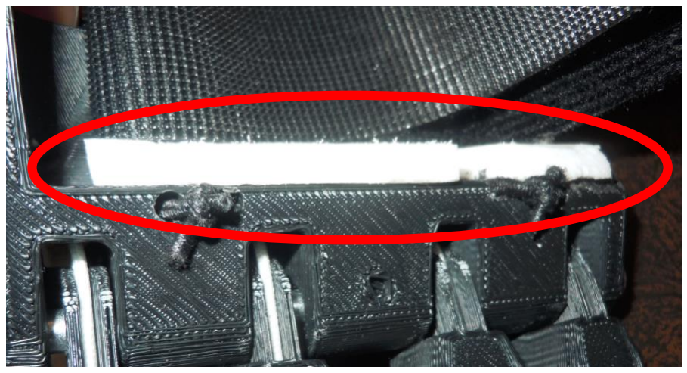
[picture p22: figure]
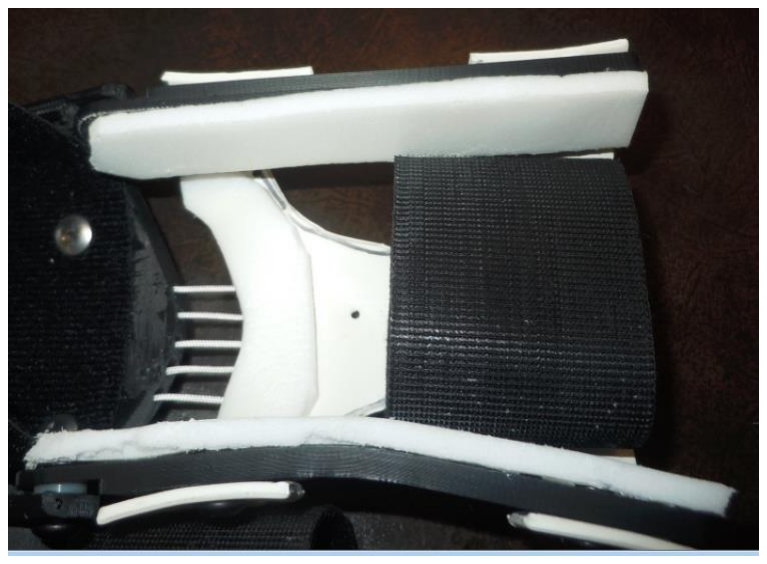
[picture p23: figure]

3. Cut 2 pieces of about 8’’ inches long of Velcro (smaller or larger depending on the forearm and hand circumference of the individual, see Figure 6). Cut another two Velcro pieces of about 6’’ and 2’’ inches long.
4. Cut 3 holes to fit the3/16" (or 1/4’’) Chicago screws posts on the two pieces of Velcro that are 8’’ inches long (Figure 6 and 7). Make sure that one piece is aligned with the holes in the hand and the other is aligned with the holes in the forearm gauntlet. Place the Chicago screws posts to ensure that the soft side of the Velcro will be in contact with the skin (Figure 8). Place these two pieces on the hand and forearm gauntlet.

Figure 4. Gauntlet with firm foam padding (both sides and on top)

Figure 5. Knuckle with firm foam padding

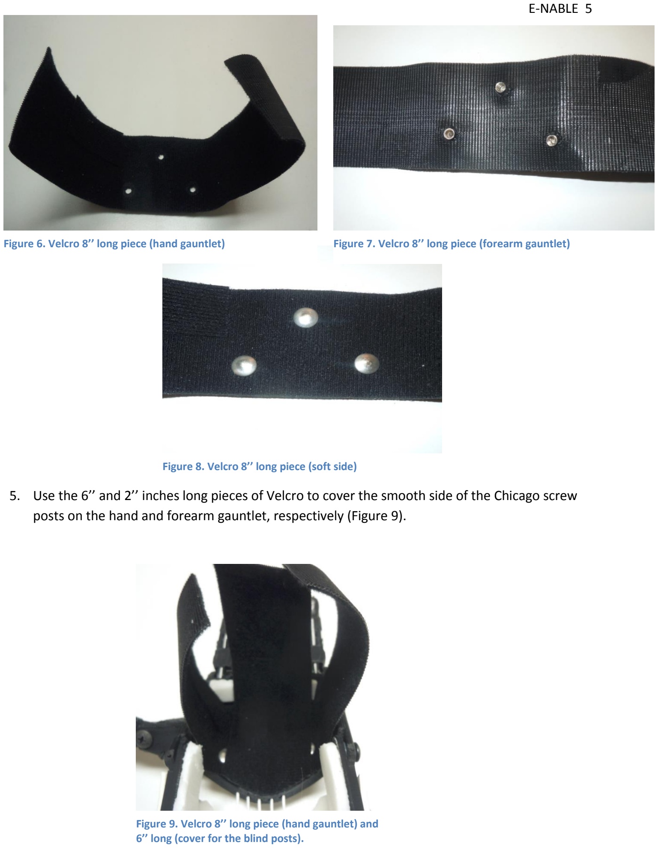
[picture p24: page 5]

5. Use the 6’’ and 2’’ inches long pieces of Velcro to cover the smooth side of the Chicago screw posts on the hand and forearm gauntlet, respectively (Figure 9).
Figure 6. Velcro 8’’ long piece (hand gauntlet) | Figure 7. Velcro 8’’ long piece (forearm gauntlet)

Figure 8. Velcro 8’’ long piece (soft side)

Figure 9. Velcro 8’’ long piece (hand gauntlet) and 6’’ long (cover for the blind posts).

6. On the wrist hinge/joint place the 3/8" Chicago screw posts and add a plastic washer (included on the STL files) between the hand and forearm gauntlet hinges.

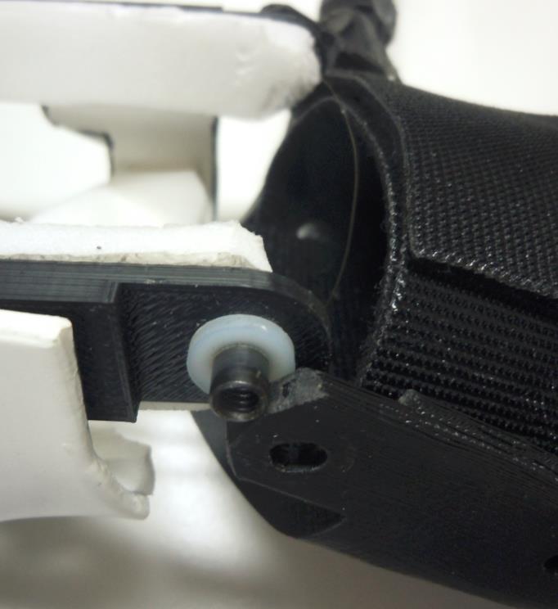
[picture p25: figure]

Elastic and Strings

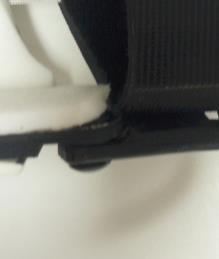
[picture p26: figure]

For these steps refer to the Snap Together Robohand instruction manuals from page 41 to 61 (Click the link below, then click download this thing and the manual is the last file “Snap_Togeather_Robohand_Instructions”).

(http://www.thingiverse.com/thing:92937).

Figure 10. wrist hinge/joint plastic washer placement

Figure 11. wrist hinge/joint completed

If you need a device made at a distance, take three pictures of your hands following these instructions.

Template for pictures for range of motion and sizing assessment

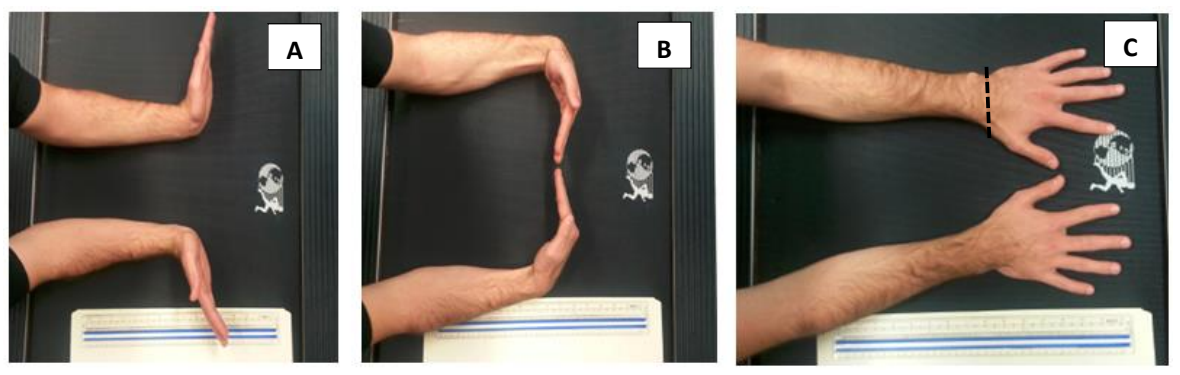
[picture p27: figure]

1. All pictures should include the entire forearm up to the elbow.
2. All pictures should be taken from directly above the arms and not at any angle.
3. Place a ruler that measures either inches or centimeters (or both) somewhere in the picture so

that lines on the ruler are visible.

4. Bend the wrists as far as possible for picture A and B.
5. Draw a line in pen on the top of the wrist of the affected hand for picture C.
6. Post these pictures on the E-NABLE site, so members of the E-NABLE group can take the needed

measurements to construct the device at no cost.

Owen’s Tensioner System

Ivan Owen took the time to make a quick video to explain the assembly and function of the tensioner system included in the forearm gauntlet of the Cyborg Beast:

http://www.youtube.com/watch?v=vimeVMZjS6E&feature=youtu.be

General Recommendations for E-NABLE Prosthetic Devices

1. As a general rule we recommend the users of these Mechanical Hands not to expose these devices to extremely hot conditions (over 250° F) or fire since they are made out of plastic.
2. Make sure there are no areas that may cause pressure or skin irritation as it may cause skin
breakdown
3. Allow the mechanical hand breathing room as excessive sweat and other components may cause poor hygiene
4. Check every 30 minutes for redness or skin irritation when first wearing the mechanical hand. If you find redness or skin irritation please stop using the Mechanical Hand.
5. Make sure you have no allergic reactions to the material use to print the mechanical hand or any other component. If you do experience allergic reactions stop using the Mechanical Hand.
6. Make sure the mechanical hand is comfortable
7. Ensure the mechanical hand is functioning for the correct purpose
8. If a child will be using it. The child needs to be supervised at all time.
9. Start using the hand in a progressive manner. If the muscles of your wrist joint are tired, it would be a good idea to take a break and continue using the mechanical hand the next day.
10. If any component of the Mechanical Hand brakes please stop using the Mechanical Hand.
11. Ensure that the screws are not loose.

Acceptance

By accepting and downloading any files, design, plan, component or assembly instructions related to the this artificial/mechanical hand “Cyborg Beast”, I understand and agree that any such information or material furnished by any individual associated with the design team is furnished as a gift for the sole purpose of evaluating various design iterations, ideas and modifications. I understand that such improvements are intended to benefit individuals having specific disabilities and are not intended for commercial use. I further understand and agree that there are no warranties expressed or implied associated with the provision of any such information or material.

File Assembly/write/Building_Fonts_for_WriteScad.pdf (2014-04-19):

p1

Harlan Martin

## Intro

Let me begin this by apologizing to everyone that uses InkScape.. These instructions are geared toward people like me that have never used it before. EVERYTHING in this help file is step by step. If there is a better way of doing it, let me know and I will revise the instructions.

Be forewarned... Making fonts is very tedious, but once you build a couple of letters, it's not very difficult. I tried to cover all the problems that I encountered while I was making fonts, but I might have missed a few. If so, contact me on Thingiverse (harlandmii) . Someone else might have the same problems.

Note: If you do take the time to build a font, PLEASE share it!!!!! I and anyone else that use it would be grateful :)

If you have problems, check the help section... I will try to keep it as updated as possible.

-o-

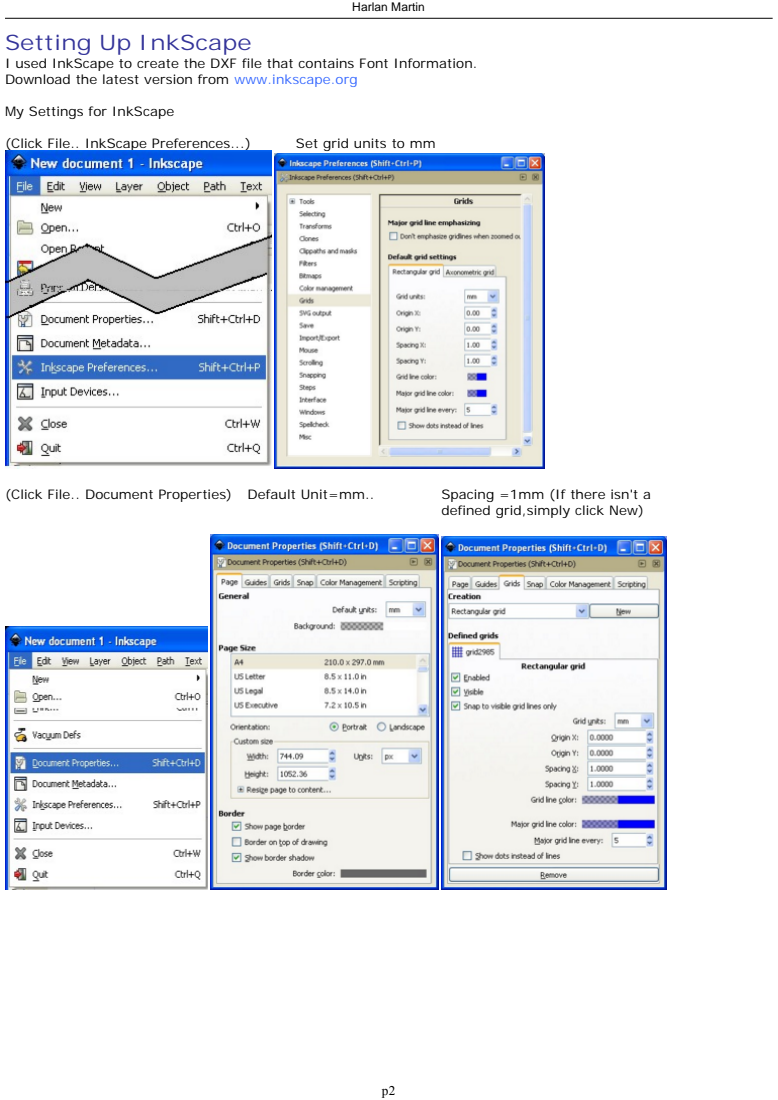
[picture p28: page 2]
(Click File.. InkScape Preferences...); Set grid units to mm; (Click File.. Document Properties); Default Unit=mm..; Spacing =1mm (If there isn't a

Setting Up InkScape
I used InkScape to create the DXF file that contains Font Information.
Download the latest version from www.inkscape.org

My Settings for InkScape

defined grid,simply click New)

To view the layers window.. (click Layer.. Layers)

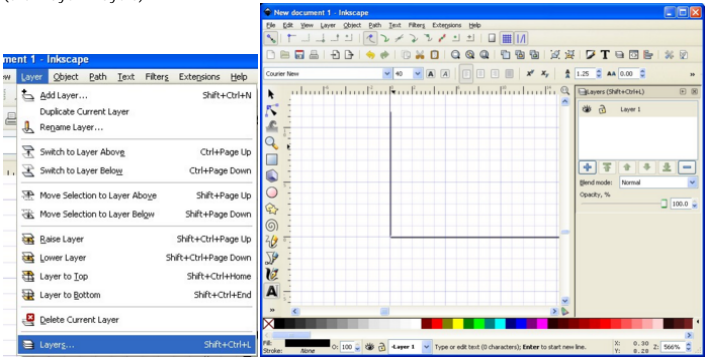
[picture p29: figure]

-o-

## Making a Guide

Click Create Text

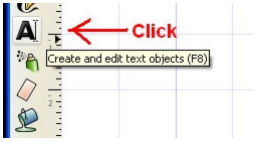
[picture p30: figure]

At the top of inkscape, Choose Desired Font and set font size to 40 (I also selected bold because courier is a thin font)

The first letter needs to be one of the larger letters, (Like capital M or W) so we can make a bounding guide to align the rest of the letters.

I am zoomed in pretty close here (1mm squares) Click in the bottom left of the page marker

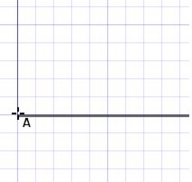
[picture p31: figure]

Type M

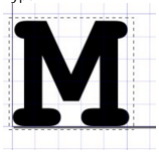
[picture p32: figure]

Use the Arrow (select and transform)
to align the letter to the left and bottom of the page marker.

Rename Layer 1 to the name of the letter

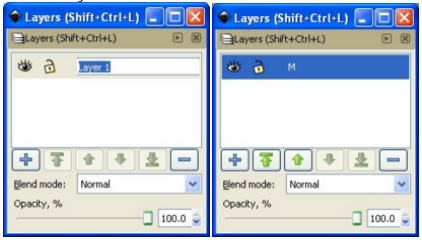
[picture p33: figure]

On the layers window, click the + to add a new layer. (Name it Border or something similar)
Use the Green Down Arrow to move it to the bottom of the list.

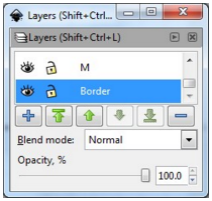
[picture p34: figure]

Make sure the Border layer is selected in the layers window. Click Create Rectangle and make a bounding box for the M
(I chose light pink)
All of the rest of the letters will be centered in this box.

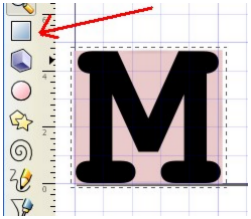
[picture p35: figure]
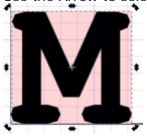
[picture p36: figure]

Use the Arrow to select the box

Click Path... Object to Path

Use Edit paths by nodes.
and select all four corners

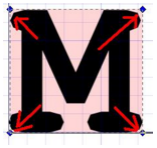
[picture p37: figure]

Click Make selected segments lines
(This process will be used on each letter to convert them to lines)

Lock the Border layer so it can't be accidentally changed.

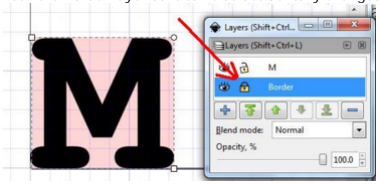
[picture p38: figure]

Choose the letter (M) Layer again..

Click the arrow (Select and transform) Click on the letter to select it

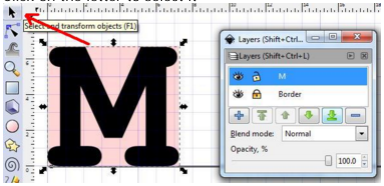
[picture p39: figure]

Click Path and Object to Path

Click Edit paths by nodes..
Then click on the letter to select it.

Drag a square around the letter to select all the nodes

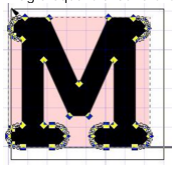
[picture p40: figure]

Click Make selected segments lines

If everything looks ok, we can go to the next letter. (If not, see the section on Making Letters Better)

-o-

## Making Letters

## Repeat the following steps for all letters and symbols

Click the + on the layers window to make a layer for
the next letter. (If its an A, name the layer A)
(lower case letter layers are named with a lower case letter and an underscore ie... the layer for lower case c would be c_ )
(layers are case sensitive)
(use the green arrows to put the layers in order if desired)

Close the eye on the M layer to hide it..
Then choose the A layer to edit

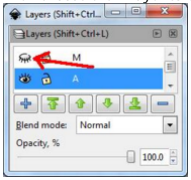
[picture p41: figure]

Choose create and edit text objects

Type the letter (A)

Use the Arrow to align it

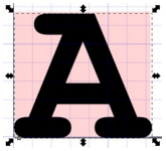
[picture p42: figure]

Click Path and Object to Path

Click edit paths by nodes
Click on the letter, then select all the nodes

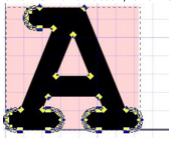
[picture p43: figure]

Click Make selected segments lines

### (That is the process for each letter)

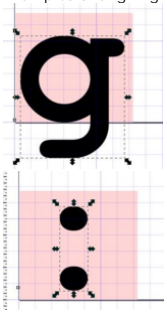
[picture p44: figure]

Examples of aligning letters

-o-

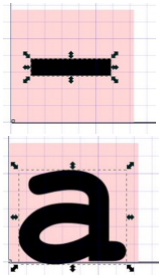
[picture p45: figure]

## Making Letters Better

Somtimes, when you click Path..Object to path, the image won't have enough points to make curved sides.

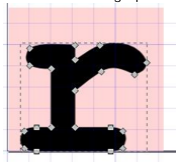
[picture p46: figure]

After you select all the nodes and click

Make Selected Segments Lines,
it becomes obvious.

If you don't like the looks of the letter, hold Ctrl and press Z to undo the change.

Click Edit paths by nodes
Select 2 or more nodes
(tip:click one node, then hold shift and click another) Then click Insert new nodes into selected segments.

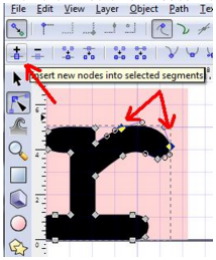
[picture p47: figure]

A new node will be on the curve.

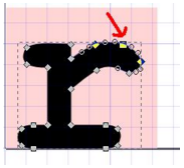
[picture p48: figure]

Repeat this process on each area that doesnt have enough
nodes to make the curves look smooth.

### NOTE: The more nodes a letter has, the slower it will draw in

OpenScad. The fewer, the better.

When your done adding nodes, select them all, and

click Make selected segments lines

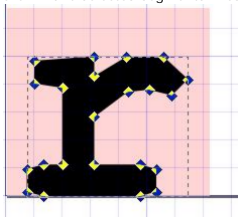
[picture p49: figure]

Move on to the next letter

-o-

## Saving the File

Be sure to save the SVG file each time.. Just click file.. Click save Name the file with the name of the font.

To use the font in OpenScad, we need to convert it to a DXF file.
Before saving the DXF, verify that all letters,boxes and shapes are converted to line segments. Otherwise, OpenScad won't be able to use it.

To make the DXF file:
Click File...
Click Save As...
Click the down arrow on save as type.. Choose Desktop Cutting Plotter(R13)(*.dxf)

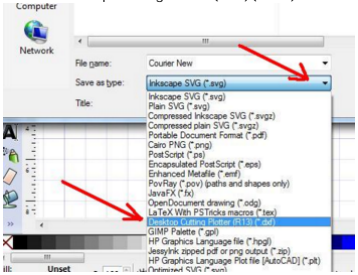
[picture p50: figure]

Click OK

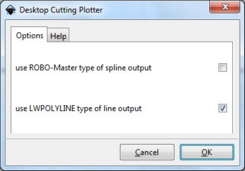
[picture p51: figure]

## Note: If you are testing a font as you create it, clear the cache on OpenScad the next time you update the Font... New letters won't appear until you do. (on OpenScad, click Design..click Flush Caches)

-o-

## HELP!!!

I will add this as soon as possible

-o-

## Testing While Making Fonts

-o-

## Font File Doesnt Work

-o-

## Some Letters Are Missing

-o-

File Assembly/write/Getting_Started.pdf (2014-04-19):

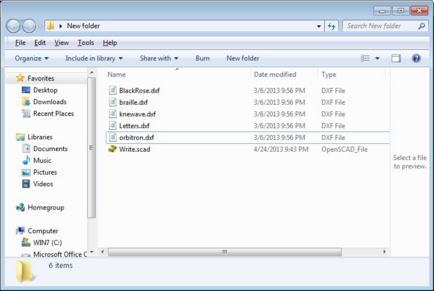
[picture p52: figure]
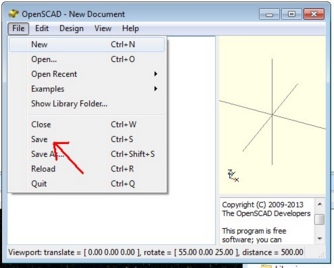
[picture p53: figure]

p1

Harlan

## Getting Started

Create a new folder on your desktop..

copy the folowing files to the new folder: Write.scad
BlackRose.dxf
braille.dxf
knewave.dxf
Letters.dxf
orbitron.dxf

Start openscad
click file.. save..

Find the new folder you created on your desktop and save your blank openscad file..

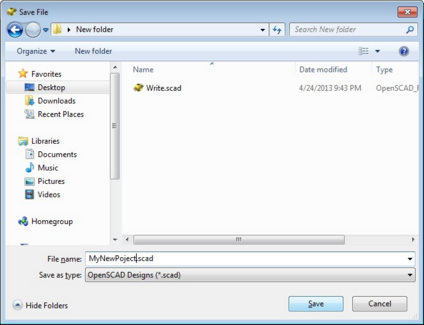
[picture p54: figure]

Your working folder (the new one you created on the desktop) will now contain write.scad, the dxf files (fonts) and your new project.

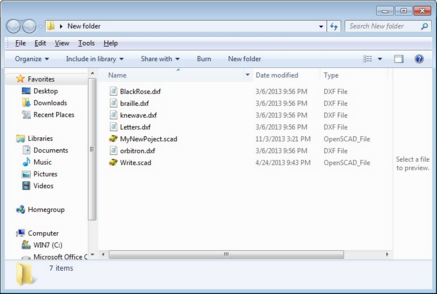
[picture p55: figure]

Now lets create an example.

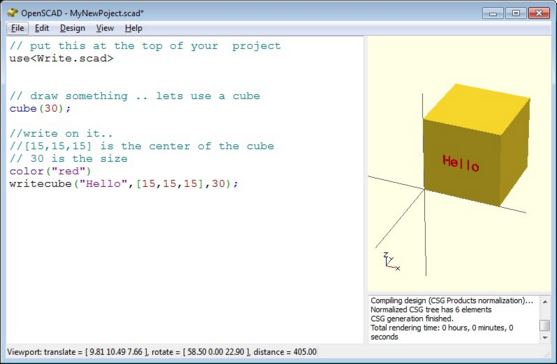
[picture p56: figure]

The use<Write.scad> tells openscad to use the routines in the write.scad file with the project you are working on..

-o-

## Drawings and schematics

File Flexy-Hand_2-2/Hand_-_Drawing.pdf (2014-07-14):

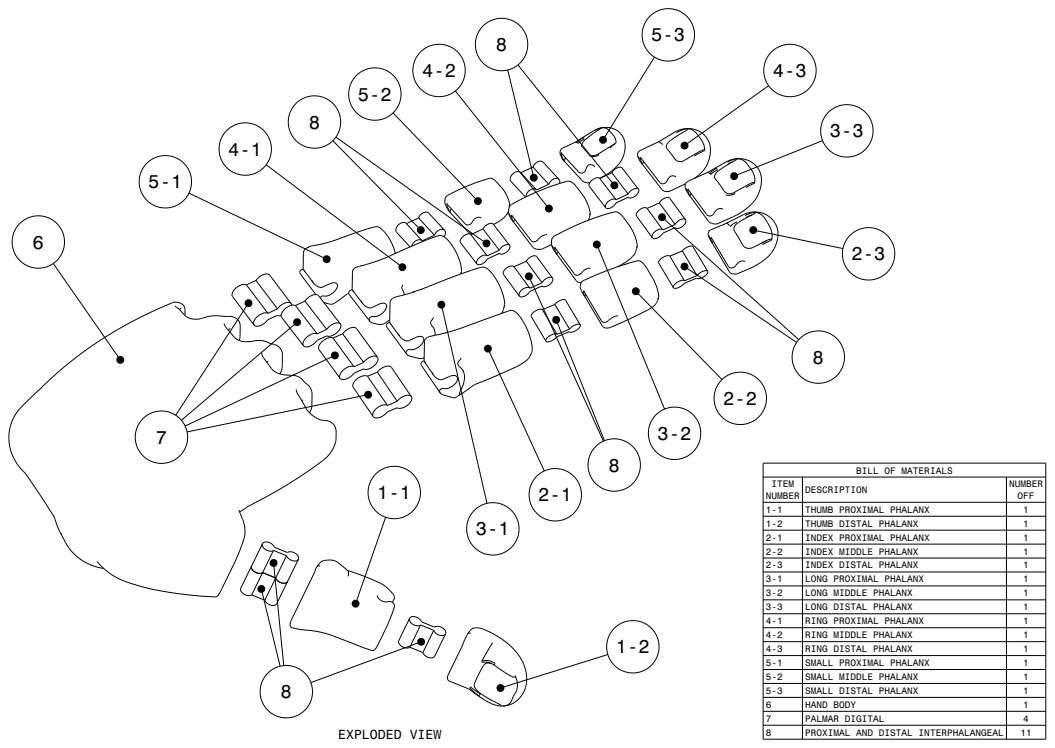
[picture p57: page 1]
EXPLODED VIEW; PROXIMAL AND DISTAL INTERPHALANGEAL

BILL OF MATERIALS

ITEM NUMBER | DESCRIPTION | NUMBER OFF

1-1 | THUMB PROXIMAL PHALANX | 1
1-2 | THUMB DISTAL PHALANX | 1
2-1 | INDEX PROXIMAL PHALANX | 1
2-2 | INDEX MIDDLE PHALANX | 1
2-3 | INDEX DISTAL PHALANX | 1
3-1 | LONG PROXIMAL PHALANX | 1
3-2 | LONG MIDDLE PHALANX | 1
3-3 | LONG DISTAL PHALANX | 1
4-1 | RING PROXIMAL PHALANX | 1
4-2 | RING MIDDLE PHALANX | 1
4-3 | RING DISTAL PHALANX | 1
5-1 | SMALL PROXIMAL PHALANX | 1
5-2 | SMALL MIDDLE PHALANX | 1
5-3 | SMALL DISTAL PHALANX | 1
6 | HAND BODY | 1
7 | PALMAR DIGITAL | 4

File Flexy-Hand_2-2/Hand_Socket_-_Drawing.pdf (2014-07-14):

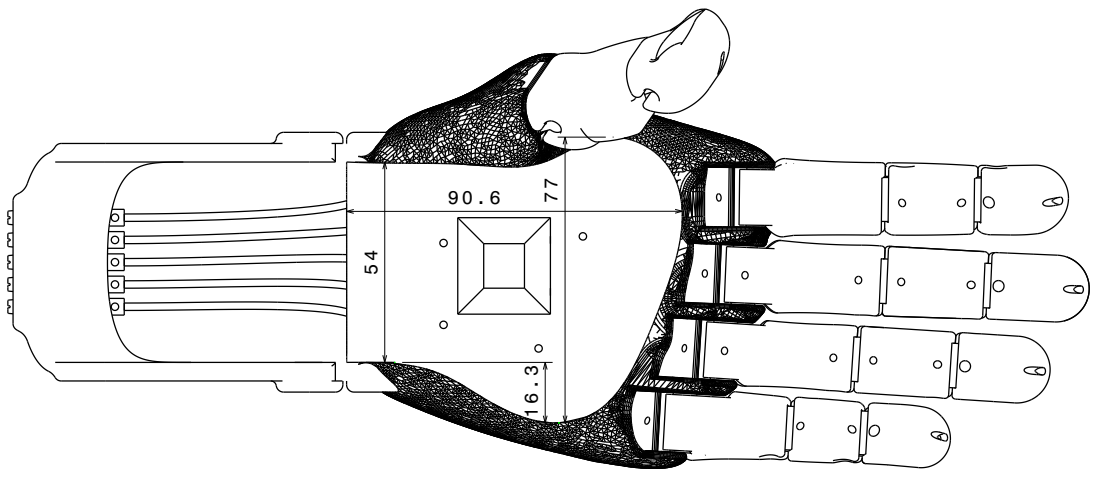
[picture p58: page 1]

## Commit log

2014-02-27 arranging, readmes
    [David-KnuckleBlock.scad, Ivan-Tuner.scad]
2014-03-14 Added David's Parametric Gauntlet
    [David-Gauntlet-5M2.stl, David-Gauntlet.scad, Include-HandParameters.scad, Include-HelperModules.scad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]
2014-03-28 Initial checkin
    Downloaded from Thingiverse, unpacked zip files, put STL files into an
    STL File directory, took dates out of folder names.
    [Cyborg Finger 1.0.blend, Cyborg Finger 1.0.stl, Cyborg Proximal Phalange 1.0.stl, Cyborg Thumb Finger 1.0.blend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]
2014-03-30 Initial OpenSCAD checkin
    Simple assembly
    [Assembly.scad]
2014-03-30 Add a 'next steps' list.
    [Assembly.scad]
2014-03-30 Moved Assembly.scad to top level of the repo
    Since the assembly pulls parts from all designs, I realized that it
    should be in the top level of the repository.
    [Assembly.scad]
2014-03-30 Changed offsets into vectors, use gauntlet params instead of scaling
    [Assembly.scad]
2014-03-30 Make it easy to test DavidGauntlet stand-alone
    [David-Gauntlet.scad]
2014-03-30 remove unused param
    [Assembly.scad]
2014-03-30 Add selection between designs. Start integrating David's parametric fingers
    [Assembly.scad, David-FingerDistal2.scad, David-FingerProximal.scad]
2014-03-31 Trying to 'pack' all of the STL files and referenced OpenSCAD files into one huge file, to work in Customizer
    It’s HUGE, and likely won’t work.
    [Assembly.scad, Cyborg Finger 1.0.scad, Cyborg Proximal Phalange 1.0.scad]
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2014-03-31 Added Jay MakerBlock's parametric Cyborg Beast palm
    And integrated into Assembly and Assembly-Packed.
    [Assembly.scad, Cyborg Finger 1.0.scad, cyborgbeast07e.scad]
2014-04-08 Moved assembly into a subdirectory, added component wrappers, added measurements.
    [Assembly.scad, Cyborg Finger 1.0.scad, Cyborg Proximal Phalange 1.0.scad, CyborgLeftPalm.scad]
2014-04-08 Add module previewArm()
    [Assembly.scad]
2014-04-08 Delete Assembly.scad
    Moved into Assembly/ directory.
    [Assembly.scad]
2014-04-08 Put in measurements from the photo, and started computing control points.
    [Assembly.scad]
2014-04-08 made control points blue
    [Assembly.scad]
2014-04-08 fixed file name capitalization for Linux
    [Assembly.scad]
2014-04-09 added some logging. made control points different colors.
    [Assembly.scad]
2014-04-09 removed extra rendering of Cyborg Beast palm
    [Assembly.scad, CyborgLeftPalm.scad, cyborgbeast07e.scad]
2014-04-13 Cyborg Beast Left Palm scale/translate
    Once this wrapper is working, use for all STL files.
    [Assembly.scad, CyborgLeftPalm.scad]
2014-04-13 move selections before measurements
    [Assembly.scad]
2014-04-13 fingers, palm and gauntlet aligned
    [Assembly.scad, CyborgLeftPalm.scad]
2014-04-13 made parametric cyborg beast palm parametric
    [Assembly.scad, CyborgLeftPalm.scad, cyborgbeast07e.scad]
2014-04-19 Upgrade to latest non-parametric Cyborg Beast
    [CyborgLeftPalm.scad]
2014-04-19 Add new version of Blender Cyborg Beast
    [Cyborg Finger 1.0.stl, Cyborg Gauntlet 1.1.stl, Cyborg Thumb Finger 1.0.stl, Cyborg Thumb phalange 1.14.stl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]
2014-04-19 print label on palm
    [Assembly.scad, BlackRose.dxf, CyborgLeftPalm.scad, Letters.dxf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]
2014-04-25 Add model arm file (not integrated yet) and trying to fix the STLs
    [Assembly.scad, CyborgLeftPalm.scad, ModelArm.scad, cyborgbeast07e.scad]
2014-04-25 wired in Mike Creuzer's Arm
    [Assembly.scad, ModelArm.scad]
2014-04-29 Added David's Second Degree Hand
    OpenSCAD scripts and STL files
    [David-SecondDegree-Finger.scad, David-SecondDegree-Finger.stl, David-SecondDegree-Gauntlet.scad, David-SecondDegree-Gauntlet.stl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]
2014-05-01 wired up individual finger part rendering for david's fingers
    [Assembly.scad, CyborgLeftPalm.scad]
2014-05-02 display percent scale over Cyborg Beast
    [CyborgLeftPalm.scad]
2014-05-02 Implemented mirroring right hand
    Mirrors all parts when rendering right hand.
    Added a few more models for later use.
    [Assembly.scad, Cyborg Gauntlet 1.2.scad, Cyborg_gauntlet_1.2__Ivan_.stl, hex_sleeve_solo.stl]
2014-05-02 Corrected offset for David's fingers
    David's fingers are now aligned when assembled
    [Assembly.scad]
2014-05-02 removed duplicate (incorrect) right arm rendering
    [ModelArm.scad]
2014-05-02 positioned David's Finger Distal properly
    [Assembly.scad]
2014-05-02 started wiring up thumbs, Binkley's STLs work
    [Assembly.scad, CyborgThumbProximal.scad, ProxThumb.stl]
2014-05-05 latest Parametric Cyborg Beast from MakerBlock
    [cyborgbeast07l.scad, cyborgfingermid002.scad, cyborgfingertip002.scad, cyborgpalm001.scad]
2014-05-06 Add comments
    [Assembly.scad]
2014-06-01 Added Cyborg Hand 1.2 and 1.3
    [Cyborg Finger 1.0.stl, Cyborg Finger 1.33.stl, Cyborg Phalange 1.33.stl, Cyborg Thumb Finger 1.0.stl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]
2014-06-01 add wrappers for cyborg beast thumb finger and phalange
    [Assembly.scad, Cyborg Finger 1.33.stl, Cyborg Phalange 1.33.stl, Cyborg Thumb Finger 1.34.stl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]
2014-06-01 finished wiring in cyborg beast thumbs
    [Assembly.scad, CyborgThumbFinger.scad, CyborgThumbPhalange.scad]
2014-06-02 Fixing what looks like an issue introduced during a merge - causes critical errors during rendering
    [Assembly.scad]
2014-06-04 hide control points, hide thumb phalange on load
    [Assembly.scad, CyborgThumbPhalange.scad]
2014-06-15 Added Creo Palm, Creo Cyborg Beast as an option for the palm (3) and fingers (3). Also added the Karuna Short Gauntlet (2).
    And verified that all render.
    Note that the original Cyborg Beast Palm and Fingers aren’t valid and
    don’t compile.
    [Assembly.scad, CB_Finger_1.33.stl, CB_Phalange_1.33.stl, CB_Thumb_Finger_1.34.stl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]
2014-06-15 Default to Karuna short gauntlet (since it's new)
    [Assembly.scad, CreoCyborgLeftPalm.scad]
2014-06-17 fix absolute path, made relative
    [KarunaGauntlet.scad]
2014-06-17 added some parameter checking and error logging
    errors written to log, and displayed in terse format.
    [CreoCyborgLeftPalm.scad]
2014-06-23 Add parametric gauntlet "wrap" design, from Andreas Bastion.
    [ParametricGauntletWrap.scad, ParametricGauntletWrapExample.stl, ParametricGauntletWrapLongerExample.stl]
2014-06-24 add cyborg beast 1.4 STL files
    [CB Finger 1.4 (bumps) non manifold.stl, CB Finger 1.41 (no bumps).stl, CB Phalange 1.4.stl, CB Thumb Finger 1.4 (bumps) non manifold.stl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]
2014-06-24 Update CyborgLeftPalm module to use the 1.4 version.
    Not ready for use yet. But getting closer.
    [CyborgLeftPalm.scad]
2014-06-26 Cyborg Beast 1.4 now works (palm and fingers), also fixed parametric gauntlet sizing
    Also got various model fingers and thumb assembly alignment working,
    scaled thumb position to match palm scaling
    [Assembly.scad, CreoCyborgLeftPalm.scad, CreoCyborgThumbFinger.scad, CreoCyborgThumbPhalange.scad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]
2014-06-30 added links to included designs.
    [Assembly.scad]
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2014-07-01 fixed Creo Cyborg Beast scaling
    [Assembly.scad]
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2014-08-23 move error warning
    [CreoCyborgLeftPalm.scad, CyborgLeftPalm.scad]
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2014-08-25 Fix scaling of "no thumb" Cyborg Beast
    And put in test measurements that match the new GUI
    [Assembly.scad, CyborgNTLeftPalm.scad]
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2014-09-23 fix scaling bugs in parts plate
    [EH2Parts.scad]
2014-09-25 more subtle scaling issues fixed
    More subtle scaling bugs fixed in the ‘plate of small things’.
    [Assembly.scad, EH2Parts.scad]
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2014-10-18 add pin scaling to tighten fit
    [EH2Parts.scad]
2014-10-18 replaced absolute path with relative path (oops)
    [EH2Parts.scad]
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2014-10-19 Scale thumb wider/shorter
    So it fits the socket even if the hand is long/thin, etc.
    [Assembly.scad]
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2014-10-25 Fix bug that caused 'gauntlet' parts not to be printed
    Fix bug that caused 'gauntlet' parts not to be printed even if a
    gauntlet is selected
    [Assembly.scad, EH2Parts.scad]
2014-10-26 fix scaling of thumb pins
    And make them blue in the preview
    [EH2Parts.scad]
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2014-10-28 Fixed some missing combinations
    [Assembly.scad]
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2014-10-28 restored label, fixed missing thumb preview for fingertip 5
    [Assembly.scad, EH2LeftPalm.scad]
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2014-11-01 fixed preview bug
    So now assembly works with only L/R8.
    [Assembly.scad]
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2014-12-29 added an 'error' object
    so script always returns something and users don’t get broken graphics.
    [Assembly.scad]
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2015-01-03 error handling for thumb parts when no thumb
    [Assembly.scad]
2015-01-03 rotate error to be more readable
    [Assembly.scad]
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2015-01-03 make error messages 'shadow'
    So users don’t get STL files of error messages
    [Assembly.scad]
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2015-01-09 subtract clearance around demo hand cross-bar
    So support shouldn’t stick to the cross-bar, making it easier to remove.
    [EH2LeftPalm.scad]
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2015-01-23 fix logging code that triggered occasional error
    [Assembly.scad, CyborgLeftPalm.scad]
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
